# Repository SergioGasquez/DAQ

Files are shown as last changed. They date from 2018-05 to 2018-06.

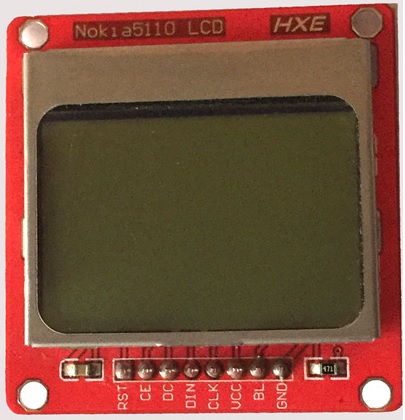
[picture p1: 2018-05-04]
LaTeX/Images/Nokia5110_Pinout.jpg

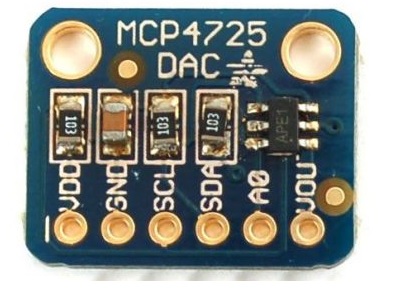
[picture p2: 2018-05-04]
LaTeX/Images/MCP4725_Pinout.jpg

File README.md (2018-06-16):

# Data Acquisition System

Here you can find everything about my final degree proyect, all the code, desings and PCB files can be found on the repository. Here is a summary of the proyect:

## General Diagram
The general diagram of the DAQ could be simplified as:

Diagram

Collected data will be avaliable in a [web developed for this purpose](https://tfg-sergio-gasquez.onlosant.com/) (An amazing IoT platform!)

## Prototypes
Two prototypes have been developed:

Propotype V1

Propotype V0

## Analog Conditioning
There are two analog conditioning parts:
- Amplifier

DAC DACanalog

-Reductor
ADC ADCanalog

Also, the MAX743 is used to power all the OP Amps in his typical configuration.

## Final product

This is the end result:

Result Propotype V1

The thesis can be also found in the repo, but sadly had to write it in spanish. If you have any doubt feel free to ask without hessitation!

## License
Copyright (c) 2017 Sergio Gasquez Licensed under the MIT license.

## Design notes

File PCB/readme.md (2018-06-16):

# PCB

## Schematic 

Schematic

## Layout 

Layout

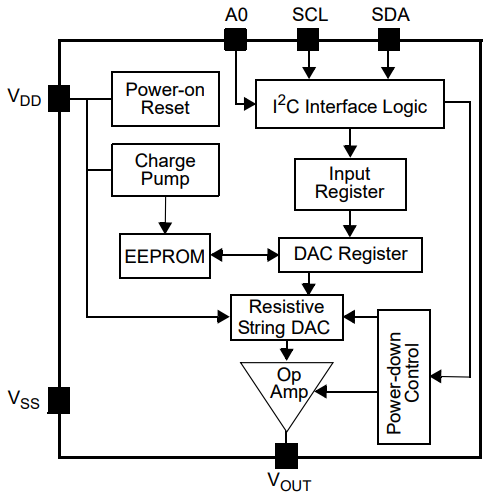
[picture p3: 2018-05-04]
LaTeX/Images/MCP4725_Schematic.PNG

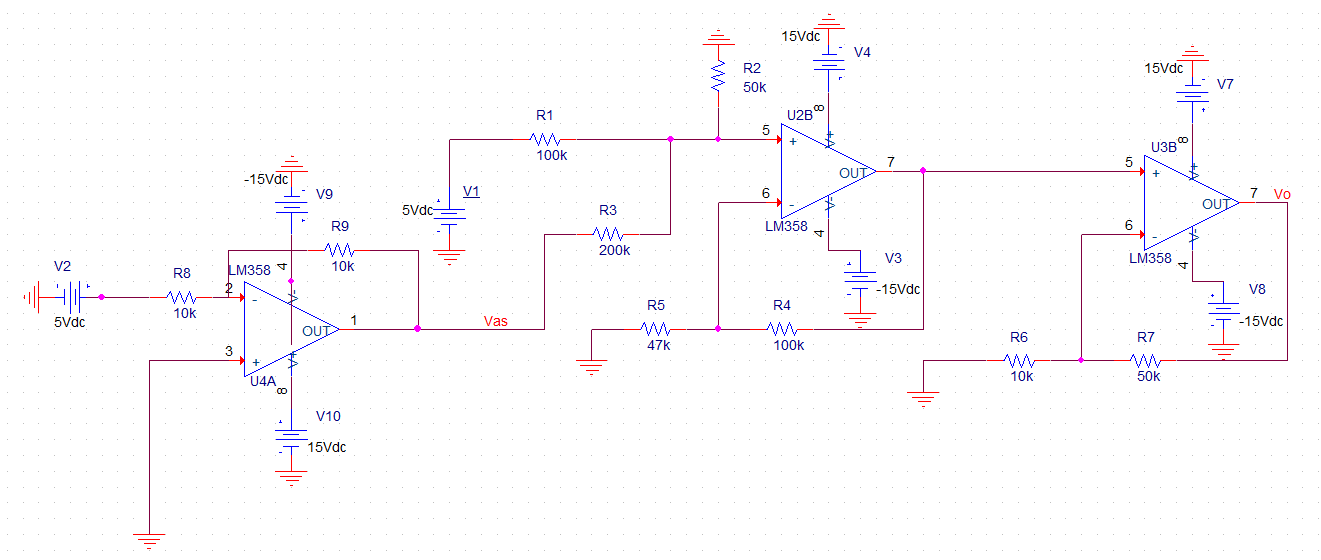
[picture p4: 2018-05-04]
LaTeX/Images/Amplificator_Schematic.PNG

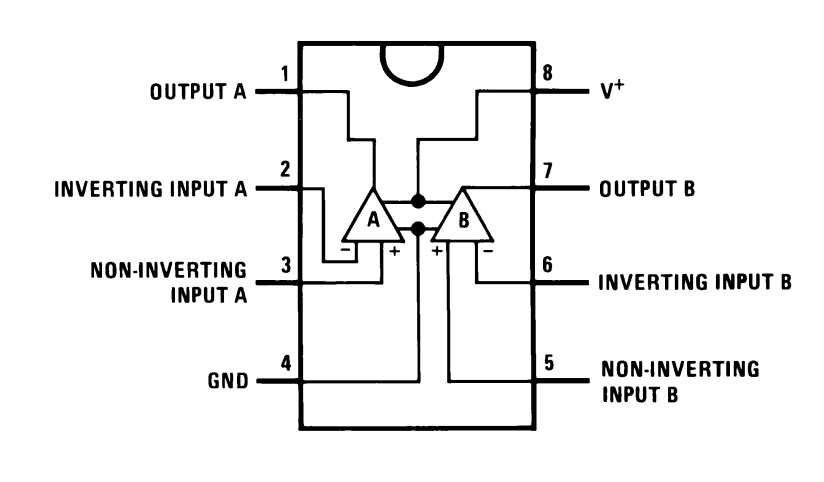
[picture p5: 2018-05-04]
LaTeX/Images/LM358_Pinout.PNG

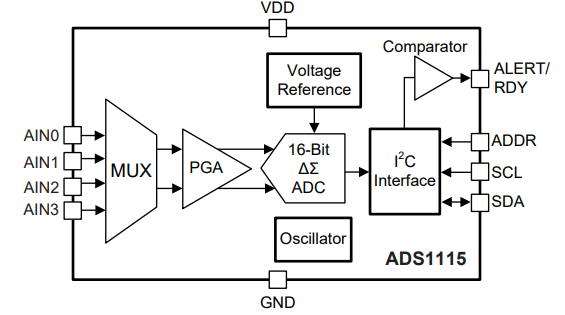
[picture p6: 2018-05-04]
LaTeX/Images/ADS1115_Schematic.PNG

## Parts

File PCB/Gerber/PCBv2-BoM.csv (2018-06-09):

Id | Designator | Package | Quantity | Designation | Supplier and ref
1 | U2 | SDShield | 1 | RTC
2 | J1 | arduino_mega_header | 1 | Arduino_Mega_Header
3 | U5 | ADC | 1 | ADC
4 | J2 | Pin_Header_Straight_1x10_Pitch2.54mm | 1 | Conn_01x10
5 | J3,J4,J7,J8,J6 | arduino_pin_socket_8 | 5 | Conn_01x08
6 | J5 | Pin_Header_Straight_2x18_Pitch2.54mm | 1 | Conn_02x18_Odd_Even
7 | U1 | Nokia5110 | 1 | NOKIA5110
8 | D3,D4,D5 | D_DO-15_P2.54mm_Vertical_AnodeUp | 3 | LM4040
9 | J9,J10,J11,J12,J13 | ScrewTerminal | 5 | Screw_Terminal_01x03
10 | R5,R14 | R-C-L-D | 2 | 200k
11 | R6 | R-C-L-D | 1 | 51k
12 | R7,R15 | R-C-L-D | 2 | 47k
13 | R8,R12,R16,R4 | R-C-L-D | 4 | 100k
14 | R9,R20,R3 | R-C-L-D | 3 | 22k
15 | R10,R11,R18,R23 | R-C-L-D | 4 | 10k
16 | R13,R19 | R-C-L-D | 2 | 50k
17 | R17 | R-C-L-D | 1 | 270k
18 | R21 | R-C-L-D | 1 | 1k
19 | R22 | R-C-L-D | 1 | 330
20 | U4 | DIP-16_W7.62mm | 1 | ADG408
21 | IC1 | DIP-16_W7.62mm | 1 | MAX743CWE+
22 | C1,C5 | Cap | 2 | 0.01uF
23 | C2 | Cap | 1 | 0.1uF
24 | C3 | Cap | 1 | 10uF
25 | C4 | Cap | 1 | 1uFC
26 | C6,C7,C11,C12,C13,C14,C15,C16,C17,C18,C19 | Cap | 11 | 100nF
27 | C8,C9,C10 | Cap | 3 | 100uF
28 | D1,D2 | R-C-L-D | 2 | D_Schottky
29 | L1,L2 | R-C-L-D | 2 | 100uH
30 | R1 | R-C-L-D | 1 | 68k
31 | R2 | R-C-L-D | 1 | 18k
32 | U6,U7,U8,U9,U10 | DIP-8_W7.62mm | 5 | LM358
33 | U11 | DAC | 1 | DAC
34 | U12 | DIP-8_W7.62mm | 1 | DG419
35 | U3 | SDShield | 1 | SDshield
36 | J14 | Pin_Header_Straight_1x05_Pitch2.54mm | 1 | Conn_01x05

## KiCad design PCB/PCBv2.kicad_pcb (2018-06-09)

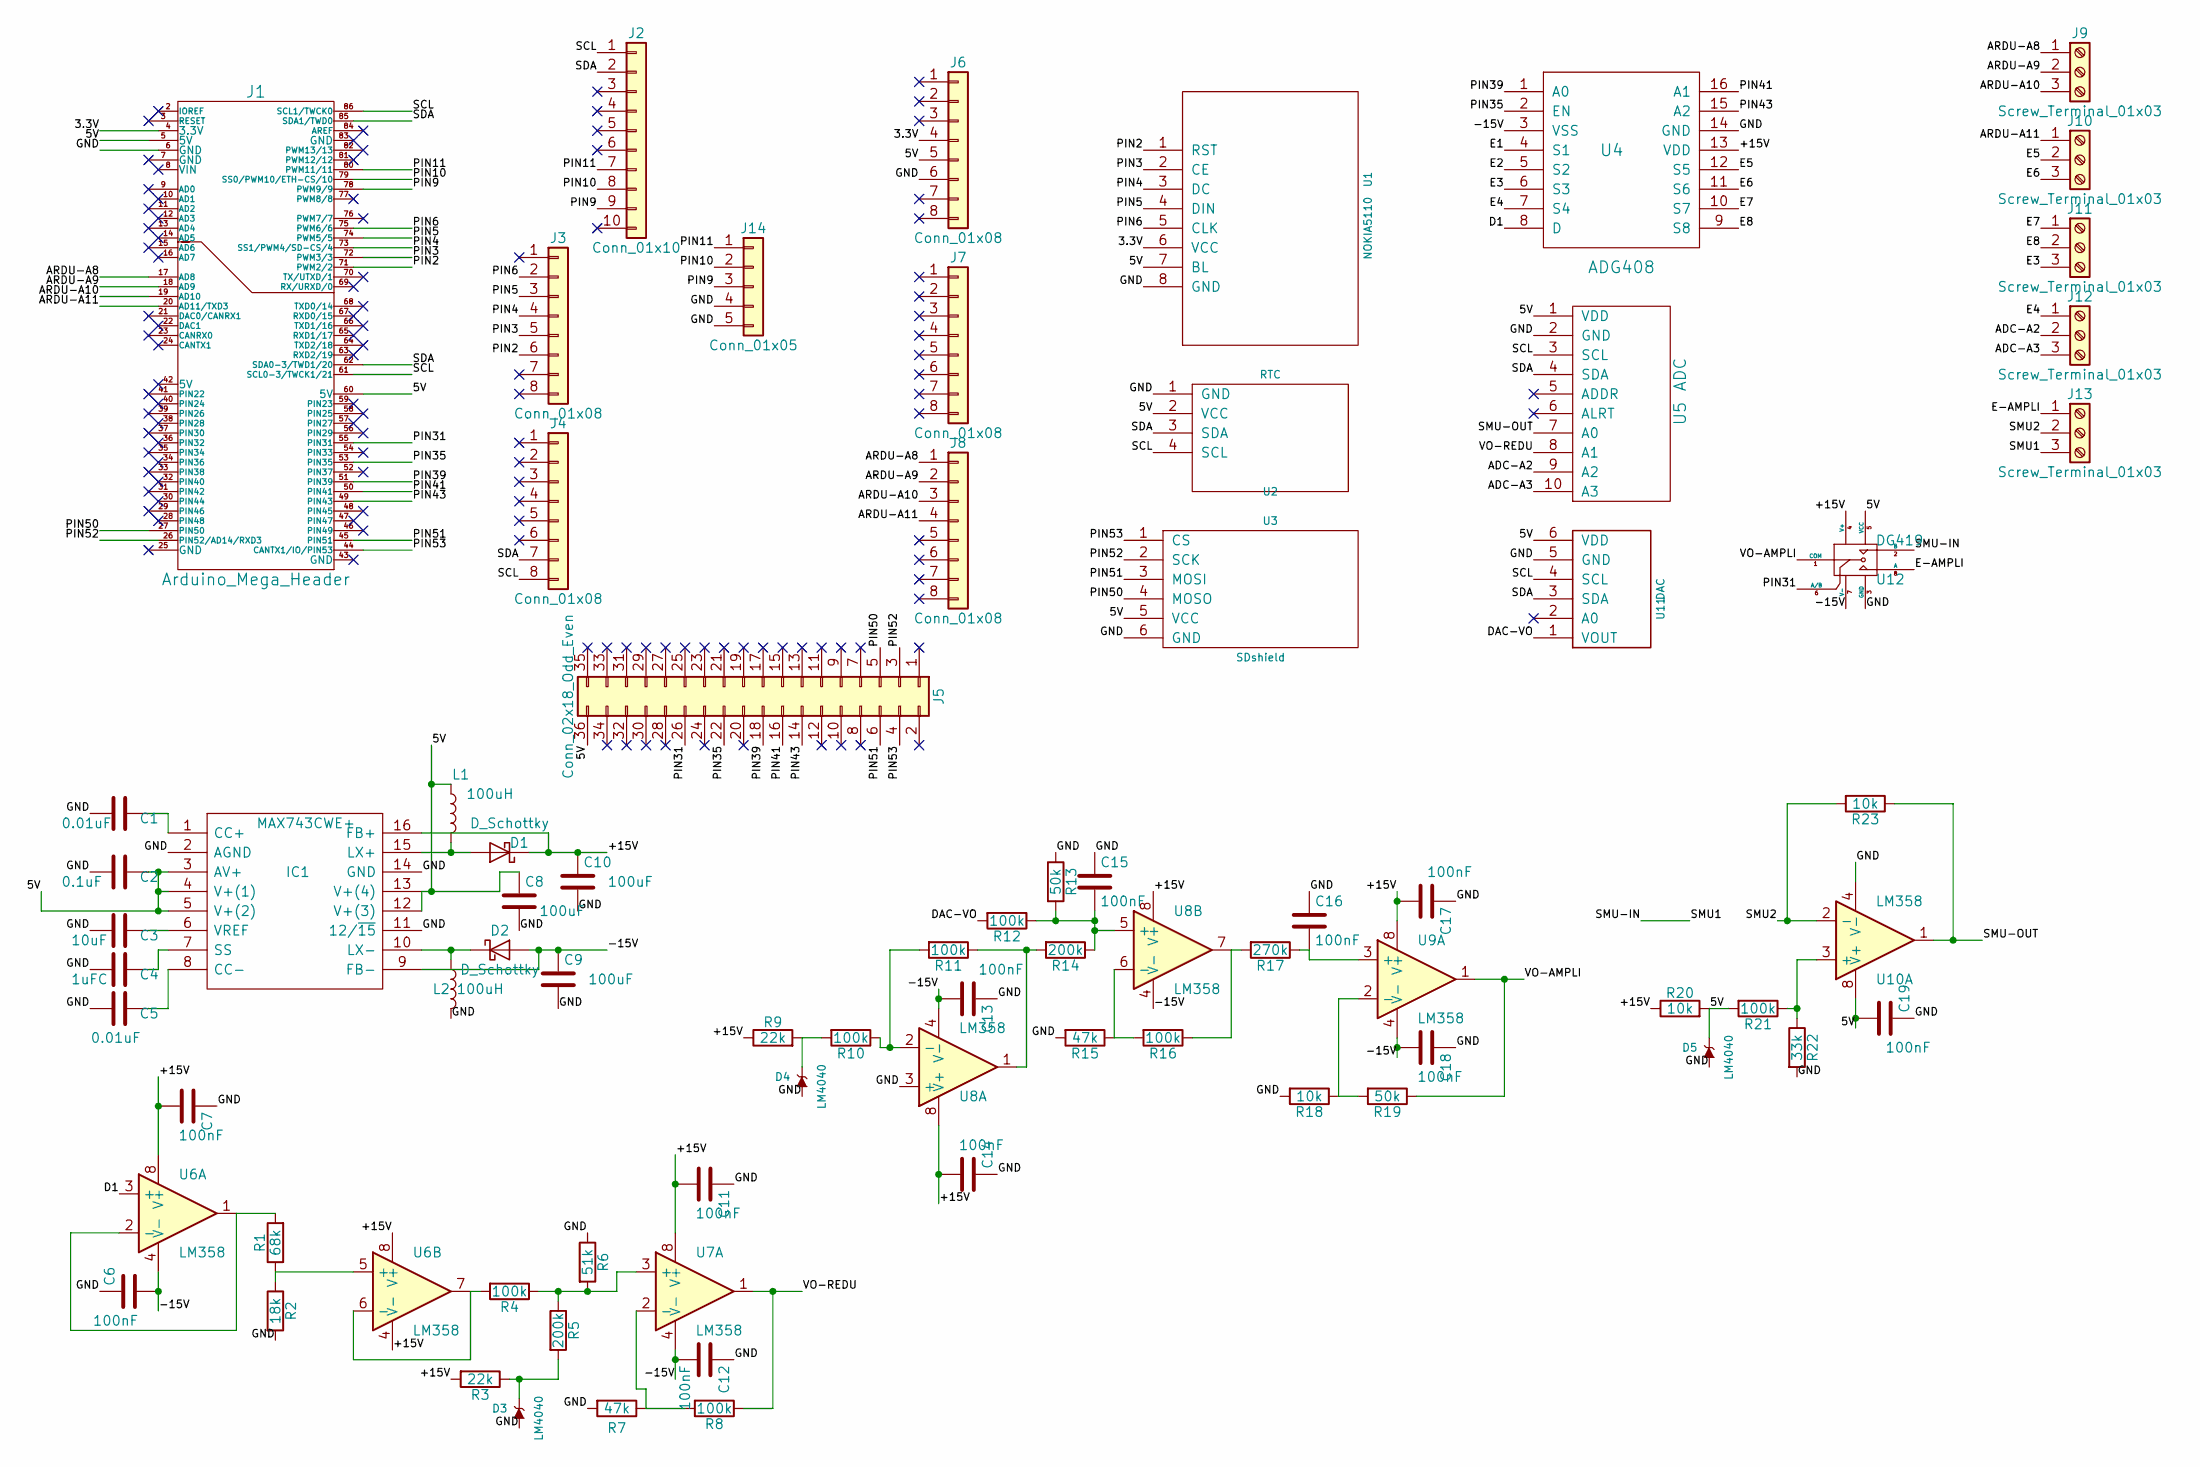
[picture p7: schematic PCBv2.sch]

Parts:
C1, C5: 0.01uF; Cap
C2: 0.1uF; Cap
C3: 10uF; Cap
C4: 1uFC; Cap
C6, C7, C11, C12, C13, C14, C15, C16, C17, C18, C19: 100nF; Cap
C8, C9, C10: 100uF; Cap
D1, D2: D_Schottky; R-C-L-D
D3, D4, D5: LM4040; D_DO-15_P2.54mm_Vertical_AnodeUp
IC1: MAX743CWE+; DIP-16_W7.62mm; Manufacturer_Part_Number MAX743CWE+
J1: Arduino_Mega_Header; arduino_mega_header
J2: Conn_01x10; Pin_Header_Straight_1x10_Pitch2.54mm
J3, J4, J6, J7, J8: Conn_01x08; arduino_pin_socket_8
J5: Conn_02x18_Odd_Even; Pin_Header_Straight_2x18_Pitch2.54mm
J9, J10, J11, J12, J13: Screw_Terminal_01x03; ScrewTerminal
J14: Conn_01x05; Pin_Header_Straight_1x05_Pitch2.54mm
L1, L2: 100uH; R-C-L-D
R1: 68k; R-C-L-D
R2: 18k; R-C-L-D
R3, R9: 22k; R-C-L-D
R4, R8, R10, R11, R12, R16, R21: 100k; R-C-L-D
R5, R14: 200k; R-C-L-D
R6: 51k; R-C-L-D
R7, R15: 47k; R-C-L-D
R13, R19: 50k; R-C-L-D
R17: 270k; R-C-L-D
R18, R20, R23: 10k; R-C-L-D
R22: 33k; R-C-L-D
U1: NOKIA5110; Nokia5110
U2: RTC; SDShield
U3: SDshield; SDShield
U4: ADG408; DIP-16_W7.62mm
U5: ADC
U6, U7, U8, U9, U10: LM358; DIP-8_W7.62mm
U11: DAC
U12: DG419; DIP-8_W7.62mm

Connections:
/3.3V: J1.4 (3.3V), J6.4, U1.6 (VCC)
/5V: C2.1, C8.1, C19.2, D5.1 (K), IC1.3 (AV+), IC1.4 (V+(1)), IC1.5 (V+(2)), IC1.12 (V+(3)), IC1.13 (V+(4)), J1.5 (5V), J1.60 (5V), J5.36, J6.5, L1.1, R20.2, R21.2, U1.7 (BL), U2.2 (VCC), U3.5 (VCC), U5.1 (VDD), U10.8 (V+), U11.6 (VDD), U12.5 (VCC)
/ADC-A2: J12.2, U5.9 (A2)
/ADC-A3: J12.3, U5.10 (A3)
/ARDU-A8: J1.17 (AD8), J8.1, J9.1
/ARDU-A9: J1.18 (AD9), J8.2, J9.2
/ARDU-A10: J1.19 (AD10), J8.3, J9.3
/ARDU-A11: J1.20 (AD11/TXD3), J8.4, J10.1
/D1: U4.8 (D), U6.3 (+)
/DAC-VO: R12.2, U11.1 (VOUT)
/E1: U4.4 (S1)
/E2: U4.5 (S2)
/E3: J11.3, U4.6 (S3)
/E4: J12.1, U4.7 (S4)
/E5: J10.2, U4.12 (S5)
/E6: J10.3, U4.11 (S6)
/E7: J11.1, U4.10 (S7)
/E8: J11.2, U4.9 (S8)
/E-AMPLI: J13.1, U12.8 (A)
/GND: C1.2, C2.2, C3.2, C4.2, C5.2, C6.1, C7.1, C8.2, C9.2, C10.2, C11.1, C12.1, C13.1, C14.1, C15.1, C16.1, C17.1, C18.1, C19.1, D3.2 (A), D4.2 (A), D5.2 (A), IC1.2 (AGND), IC1.11 (12/~15), IC1.14 (GND), J1.6 (GND), J6.6, J14.4, J14.5, L2.2, R2.2, R6.1, R7.2, R13.1, R15.2, R18.2, R22.2, U1.8 (GND), U2.1 (GND), U3.6 (GND), U4.14 (GND), U5.2 (GND), U8.3 (+), U10.4 (V-), U11.5 (GND), U12.3 (GND)
/PIN2: J1.71 (PWM2/2), J3.6, U1.1 (RST)
/PIN3: J1.72 (PWM3/3), J3.5, U1.2 (CE)
/PIN4: J1.73 (SS1/PWM4/SD-CS/4), J3.4, U1.3 (DC)
/PIN5: J1.74 (PWM5/5), J3.3, U1.4 (DIN)
/PIN6: J1.75 (PWM6/6), J3.2, U1.5 (CLK)
/PIN9: J1.78 (PWM9/9), J2.9, J14.3
/PIN10: J1.79 (SS0/PWM10/ETH-CS/10), J2.8, J14.2
/PIN11: J1.80 (PWM11/11), J2.7, J14.1
/PIN31: J1.55 (PIN31), J5.26, U12.6 (A/B)
/PIN35: J1.53 (PIN35), J5.22, U4.2 (EN)
/PIN39: J1.51 (PIN39), J5.18, U4.1 (A0)
/PIN41: J1.50 (PIN41), J5.16, U4.16 (A1)
/PIN43: J1.49 (PIN43), J5.14, U4.15 (A2)
/PIN50: J1.27 (PIN50), J5.5, U3.4 (MOSO)
/PIN51: J1.45 (PIN51), J5.6, U3.3 (MOSI)
/PIN52: J1.26 (PIN52/AD14/RXD3), J5.3, U3.2 (SCK)
/PIN53: J1.44 (CANTX1/IO/PIN53), J5.4, U3.1 (CS)
/SCL: J1.61 (SCL0-3/TWCK1/21), J1.86 (SCL1/TWCK0), J2.1, J4.8, U2.4 (SCL), U5.3 (SCL), U11.4 (SCL)
/SDA: J1.62 (SDA0-3/TWD1/20), J1.85 (SDA1/TWD0), J2.2, J4.7, U2.3 (SDA), U5.4 (SDA), U11.3 (SDA)
/SMU2: J13.2, R23.2, U10.2 (-)
/SMU-IN: J13.3, U12.2 (B)
/SMU-OUT: R23.1, U5.7 (A0), U10.1
/VO-AMPLI: R19.1, U9.1, U12.1 (COM)
/VO-REDU: R8.1, U5.8 (A1), U7.1
unnamed: C1.1, IC1.1 (CC+)
unnamed: C3.1, IC1.6 (VREF)
unnamed: C4.1, IC1.7 (SS)
unnamed: C5.1, IC1.8 (CC-)
unnamed: C15.2, R12.1, R13.2, R14.1, U8.5 (+)
unnamed: C16.2, R17.1, U9.3 (+)
unnamed: D1.2 (A), IC1.15 (LX+), L1.2
unnamed: D2.1 (K), IC1.10 (LX-), L2.1
unnamed: D3.1 (K), R3.1, R5.2
unnamed: D4.1 (K), R9.2, R10.2
unnamed: R1.1, R2.1, U6.5 (+)
unnamed: R1.2, U6.1, U6.2 (-)
unnamed: R4.1, R5.1, R6.2, U7.3 (+)
unnamed: R4.2, U6.6 (-), U6.7
unnamed: R7.1, R8.2, U7.2 (-)
unnamed: R10.1, R11.2, U8.2 (-)
unnamed: R11.1, R14.2, U8.1
unnamed: R15.1, R16.2, U8.6 (-)
unnamed: R16.1, R17.2, U8.7
unnamed: R18.1, R19.2, U9.2 (-)
unnamed: R21.1, R22.1, U10.3 (+)

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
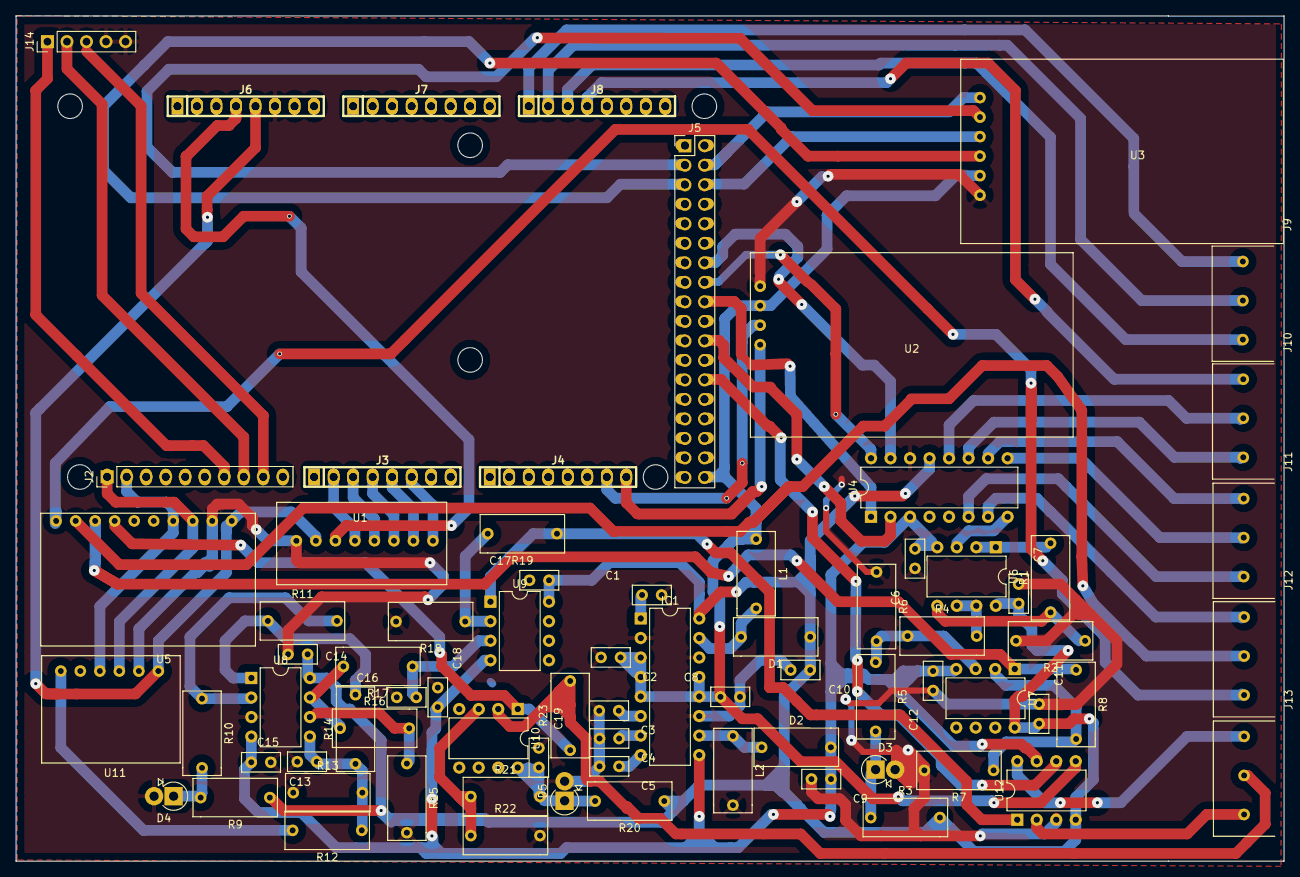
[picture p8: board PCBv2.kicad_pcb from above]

Board: 2 copper layers, 165.1 x 110.0 mm, 76 parts (1 on the bottom side), 65 nets.

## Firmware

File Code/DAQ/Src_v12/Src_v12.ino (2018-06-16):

/*
           Data Acquisition System
            Sergio Gasquez Arcos


       https://github.com/SergioGasquez/DAQ


*/

//-------------- DEFINES --------------//
#define LCD
#define RTC
#define microSD
#define ADC
#define DAC
#define MULTIPLEXER
#define MULTIPLEXER2
#define MEM_EEPROM
//#define COMGPRS
#define DEBUGGING true

//-------------- TIMERS --------------//
#define WTDG_CYCLES  10
#define COMM_TIME 60     // Time between comms (in seconds)
#define SD_TIME 1200    // Time between saves in the SD (in seconds)

#define maxCyclesComm (COMM_TIME/8)
#define maxCyclesSD (SD_TIME/8)



#include <Wire.h>
#include <avr/wdt.h>
#include <avr/sleep.h>


//-------------- SD --------------//
#ifdef microSD
#include <SPI.h>
#include <SD.h>
int pinCS = 53;
#endif //microSD


//-------------- GPRS --------------//
#ifdef COMGPRS
#include <SoftwareSerial.h>
SoftwareSerial SIM900(10, 11); // (RX, TX)
#endif //GPRS


//-------------- WTDG --------------//
volatile int ISRCounterWTDG = 0;


//-------------- ADC --------------//
#ifdef ADC
#include <Adafruit_ADS1015.h>
Adafruit_ADS1115 ads(0x48);     // ADC 0x48 is the default address
#endif //ADC

//-------------- DAC --------------//
#ifdef DAC
#include <Adafruit_MCP4725.h>
Adafruit_MCP4725 dac;
#endif //DAC

//-------------- RTC --------------//
#ifdef RTC
#include "RTClib.h"             // A5 ->SCL   A4 ->SDA
RTC_DS3231 rtc;
#endif //RTC

//-------------- LCD --------------//
#ifdef LCD
#include<LCD5110_Graph.h>
LCD5110 myGLCD(6, 5, 4, 2, 3);  // myGLCD(CLK,DIN,DC,RST,CE)
#endif //LCD

//-------------- MULTIPLEXER --------------//
#ifdef MULTIPLEXER
int enablePin = 35;
int multiplexerA0 = 39;
int multiplexerA1 = 41;
int multiplexerA2 = 43;
#endif //MULTIPLEXER

#ifdef MULTIPLEXER2
int multiplexer2Pin = 31;
#endif //MULTIPLEXER2


// File for SD
#ifdef microSD
File myFile;                      // Declare global file
String fileNameStr;               // File of the .txt
char fileName[12];

unsigned int sdCycles = 0;
volatile bool flagSD = true;
#endif //microSD

// Global Variables for date and time
#ifdef RTC
byte dayRTC;
byte monthRTC;
int yearRTC;
byte hoursRTC;
byte minutesRTC;
byte secondsRTC;
#endif //RTC

// Fonts and autonomous mode boolean
#ifdef LCD
extern uint8_t SmallFont[];
extern unsigned char TinyFont[];
bool autonomousMode = true;
#endif //LCD




#ifdef COMGPRS
unsigned int commCycles = 0;
volatile bool commFlag = false;
#endif // COMGPRS

char confStr1[9] = "9";
char confStr2[10] = "9";

// Cofiguration Variables
boolean smu = true;
boolean typeSMU = true;
boolean typeSignal = true;
boolean ADC_2 = true;
boolean ADC_3 = true;
boolean ARDU_A8 = true;
boolean ARDU_A9 = true;
boolean ARDU_A10 = true;
boolean ARDU_A11 = true;
boolean multi_E5 = true;
boolean multi_E6 = true;
boolean multi_E7 = true;
boolean multi_E8 = true;
boolean multi_E3 = true;
boolean multi_E4 = true;
byte operatingMode = 0;


// Channels values
int valSMU = 0;
int valADC_2 = 0;
int valADC_3 = 0;
int valArdu_A8 = 0;
int valArdu_A9 = 0;
int valArdu_A10 = 0;
int valArdu_A11 = 0;
int valMulti_E5 = 0;
int valMulti_E6 = 0;
int valMulti_E7 = 0;
int valMulti_E8 = 0;
int valMulti_E3 = 0;
int valMulti_E4 = 0;
int dacVal = 0;



//-------------- FUNCTIONS --------------//
void(* ResetSW) (void) = 0;


/*        Watchdog Interrup Function
   ----------------------------------------
   Each time watcdog interrupt is triggered
   (and it will be triggered each 8 secs)
   this function will run.

   We increment in 1 all the counters and if
   any counter has reach his max, it activates
   the flag.

*/

ISR (WDT_vect)
{
  ISRCounterWTDG++;
#if DEBUGGING
  //Serial.print("WTDG: ");Serial.println(ISRCounterWTDG);
#endif //DEBUGGING
  if (ISRCounterWTDG >= WTDG_CYCLES)
  {
    delay(50);
    ISRCounterWTDG = 0;
#if DEBUGGING
    Serial.println("Reset due to WTDG");
#endif //DEBUGGING
    delay(1000);
    ResetSW();
  }
#ifdef COMGPRS
  commCycles++;
  if (commCycles >= maxCyclesComm)
  {
    commFlag = true;
    commCycles = 0;
#if DEBUGGING
    //Serial.println("commFlag");
#endif //DEBUGGING  
  }
#if DEBUGGING
  //Serial.print("commCycles: "); Serial.println(commCycles);
#endif //DEBUGGING  
#endif //COMGPRS

#ifdef microSD
  sdCycles++;
#if DEBUGGING
  //Serial.print("sdCycles: "); Serial.println(sdCycles);
#endif //DEBUGGING
  if (sdCycles >= maxCyclesSD)
  {
    flagSD = true;
    sdCycles = 0;
#if DEBUGGING
    //Serial.print("flagSD: "); Serial.println(flagSD);
#endif //DEBUGGING  
  }
#endif //microSD
}// Final ISR

/*                Flash
   ----------------------------------------
   It makes the builtin flash in order
   to debug without a Serial Monitor
*/

void flash()
{
  digitalWrite(13, HIGH);
  delay(500);
  digitalWrite(13, LOW);
  delay(500);
}

void setup()
{
  Serial.begin(9600);
  delay(500);
#ifdef RTC
  initRTC();
#endif //RTC


#ifdef DAC
  dac.begin(0x62);        // Default address for MCP4725A1
  delay(500);
  //dac.setVoltage(1640, false);

#endif //DAC

#ifdef ADC
  ads.begin();
  delay(500);
#endif //ADC

#ifdef LCD
  myGLCD.InitLCD();
  myGLCD.setFont(SmallFont);
  randomSeed(analogRead(7));
  delay(100);
  updateTaskLCD(0);
#endif //LCD

#ifdef COMGPRS
  initSIM900();
  delay(1000);
#endif //COMGPRS
  setWatchdog();

#ifdef MEM_EEPROM
  checkIfConnected();
  configureSystem();
#endif // MEM_EEPROM

#ifdef microSD
  initSD();
#endif //microSD


#ifdef MULTIPLEXER
  initMultiplexer();
#endif // MULTIPLEXER
  flash();
#ifdef COMGPRS
  if (strlen(confStr1) > 2)
  {
    sendConfig();
  }
#endif //COMGPRS
}

void loop()
{
  if (operatingMode == 0)
  {
    ResetWTDG();
    cpuSleep();
#ifdef COMGPRS
    if (commFlag)
    {
      updateTaskLCD(1);
      ResetWTDG();
      commFlag = false;
#if DEBUGGING
      Serial.println("Data will be sent...");
#endif DEBUGGING
#ifdef LCD
      updateTaskLCD(3);
#endif // LCD
      measureChannels();
      delay(1000);
#ifdef LCD
      updateTaskLCD(1);
#endif // LCD
      sendData();
#ifdef LCD
      updateConfigLCD();
#endif // LCD
    }
#endif // COMGPRS

#ifdef microSD
    if (flagSD)
    {
      ResetWTDG();
      flagSD = false;
#if DEBUGGING
      Serial.println("Data will be saved in the SD Card");
#endif //DEBUGGING
#ifdef LCD
      updateTaskLCD(3);
#endif // LCD
      measureChannels();
      delay(2000);
      updateTaskLCD(2);
      getTime();
      saveToSD();
      delay(2000);
#ifdef LCD
      updateConfigLCD();
#endif// LCD;
    }
#endif //microSD
  }
  if (operatingMode == 1)     // Voltage Sweep
  {
    Serial.println("Voltage Sweep");
    int counter;
    for (counter = 0; counter < 20; counter++)
    {
      ResetWTDG();
#if DEBUGGING
      Serial.print("dacVal: "); Serial.println(dacVal);
#endif //DEBUGGIN
      dacVal = counter * 100;
      dac.setVoltage(dacVal, false);
      getTime();
#ifdef LCD
      updateTaskLCD(3);
#endif// LCD;
      measureChannels();
#ifdef LCD
      updateTaskLCD(1);
#endif// LCD;
#ifdef COMGPRS
      sendData();
#endif // COMGPRS
#ifdef LCD
      updateTaskLCD(2);
#endif// LCD;
      saveToSD();
    }
  }

  if (operatingMode == 2)       // Generate Wave form
  {
    if (typeSignal)
    {
      generateWaveform(0);
    }
    if (!typeSignal)
    {
      generateWaveform(1);
    }
  }

}

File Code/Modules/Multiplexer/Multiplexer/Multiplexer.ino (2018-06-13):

int enablePin = 35;
int multiplexerA0 = 39;
int multiplexerA1 = 41;
int multiplexerA2 = 43;



void initMultiplexer()
{
  pinMode(enablePin, OUTPUT);
  pinMode(multiplexerA0, OUTPUT);
  pinMode(multiplexerA1, OUTPUT);
  pinMode(multiplexerA2, OUTPUT);

  digitalWrite(enablePin, HIGH);
  Serial.println("Multiplexer Initialized");
}


/*              setChannel
   ----------------------------------------
   Funtion that selects which channel of
   the multiplexer will be conected to
   the output.
*/
void setChannel(byte channel)
{                        
  if (channel == 1)
  {
    digitalWrite(multiplexerA0, LOW);
    digitalWrite(multiplexerA1, LOW);
    digitalWrite(multiplexerA2, LOW);
  }
  else if (channel == 2)
  {
    digitalWrite(multiplexerA0, HIGH);
    digitalWrite(multiplexerA1, LOW);
    digitalWrite(multiplexerA2, LOW);
  }
  else if (channel == 3)
  {
    digitalWrite(multiplexerA0, LOW);
    digitalWrite(multiplexerA1, HIGH);
    digitalWrite(multiplexerA2, LOW);
  }
  else if (channel == 4)
  {
    digitalWrite(multiplexerA0, HIGH);
    digitalWrite(multiplexerA1, HIGH);
    digitalWrite(multiplexerA2, LOW);
  }
  else if (channel == 5)
  {
    digitalWrite(multiplexerA0, LOW);
    digitalWrite(multiplexerA1, LOW);
    digitalWrite(multiplexerA2, HIGH);
  }
  else if (channel == 6)
  {
    digitalWrite(multiplexerA0, HIGH);
    digitalWrite(multiplexerA1, LOW);
    digitalWrite(multiplexerA2, HIGH);
  }
  else if (channel == 7)
  {
    digitalWrite(multiplexerA0, LOW);
    digitalWrite(multiplexerA1, HIGH);
    digitalWrite(multiplexerA2, HIGH);
  }
  else if (channel == 8)
  {
    digitalWrite(multiplexerA0, HIGH);
    digitalWrite(multiplexerA1, HIGH);
    digitalWrite(multiplexerA2, HIGH);
  }
  else
  {
    Serial.println("Error. Wrong channel");
  }
}

void setup() {
  initMultiplexer();
  Serial.begin(9600);
}

void loop() {
  Serial.println("5");
  setChannel(5);
  delay(5000);
  Serial.println("6");
  setChannel(6);
  delay(5000);
  Serial.println("7");
  setChannel(7);
  delay(5000);
  Serial.println("8");
  setChannel(8);
  delay(5000);
  Serial.println("3");
  setChannel(3);
  delay(5000);
  Serial.println("4");
  setChannel(3);
  delay(5000);

  
}

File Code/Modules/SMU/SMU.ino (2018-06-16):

/**************************************************************************/
/*!
    @file     trianglewave.pde
    @author   Adafruit Industries
    @license  BSD (see license.txt)

    This example will generate a triangle wave with the MCP4725 DAC.

    This is an example sketch for the Adafruit MCP4725 breakout board
    ----> http://www.adafruit.com/products/935

    Adafruit invests time and resources providing this open source code,
    please support Adafruit and open-source hardware by purchasing
    products from Adafruit!
*/
/**************************************************************************/
#include <Wire.h>
#include <Adafruit_MCP4725.h>
#include <Adafruit_ADS1015.h>

Adafruit_MCP4725 dac;
/*DAC*/
Adafruit_ADS1115 ads(0x48);
float Voltage = 0.0;
int multiplexer2Pin = 31;


int  dacVal;

void setup(void) {
  Serial.begin(9600);

  dac.begin(0x62); // Default address for MCP4725A1

  ads.begin();    // Initalice the adc

  //pinMode(multiplexer2Pin, OUTPUT);
  //digitalWrite(multiplexer2Pin, LOW);

}


float readADC(int channel)
{
  float aux = 0;
  int i = 0;
  for (i = 0; i <= 99; i++)
  {
    aux += ads.readADC_SingleEnded(channel);
  }
  aux = aux / 100;
  return aux;
}

void loop(void) {
  uint32_t counter;
  float valADC_A0;
  float voltage;
  counter = 0;
  //  for (counter = 0; counter < 9; counter++)  // Ramp       [-15,0] V
  //  {
  //    dacVal = counter * 205;
  //    Serial.print(" \tDAC: "); Serial.print(dacVal);
  //    dac.setVoltage(dacVal, false);
  //    delay(500);
  //    valADC_A0 = readADC(0);
  //    Serial.print(" \t ");Serial.println(valADC_A0);
  //  }
  valADC_A0 = readADC(2);
  //voltage = valADC_A0 * 0.1875;

  Serial.println(valADC_A0);
  //Serial.print("\t temp: "); Serial.println(voltage/10);

  delay(100);


  dacVal = 1650;
    for (counter = 0; counter < 25; counter++)  // Ramp       [-5,0] V
    {
      Serial.print(counter);
      dacVal += 2;
      Serial.print(" \tDAC: "); Serial.print(dacVal);
      dac.setVoltage(dacVal, false);             // We set the voltage at the counter valuex
      delay(500);
      valADC_A0 = readADC(0);
      voltage = valADC_A0 * 0.1875 / 1000;
      Serial.print("\t voltage: "); Serial.println(voltage);
  
    }
}

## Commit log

2018-03-11 Change of the structure and add PCB schematic
    [DAQ.kicad_pcb, DAQ.sch]
2018-03-12 PCB Improvement
    [DAQ.kicad_pcb, DAQ.sch]
2018-03-16 PCB Improvements
    [DAQ.kicad_pcb, DAQ.sch]
2018-03-16 Add ground plane,max743 and started analogic conditioner
    [DAQ.kicad_pcb, DAQ.sch]
2018-03-20 Analog Conditioner added int PCB layout
    [DAQ.kicad_pcb, DAQ.sch]
2018-04-03 Changed RTC module on PCB
    [DAQ.kicad_pcb, DAQ.sch]
2018-04-05 Add simulations of the analog part after the DAC
    [AMPLIFIER.DSN, DAQANALOGIC.DSN, LEVELSHIFTER.DSN]
2018-04-05 Improvements on the PCB
    [DAQ.kicad_pcb, DAQ.sch]
2018-04-06 Changes on simulations
    [DAQANALOGIC.DSN]
2018-04-10 Added analog part of DAC to PCB
    [DAQ.kicad_pcb, DAQ.sch]
2018-04-17 Analog parts of the PCB upgraded
    [DAQ.kicad_pcb, DAQ.sch, DAQANALOGIC.DSN]
2018-04-18 PCB Upgraded and screens of the DAC analog
    [DAC_Original_-15to15.CSV, DAC_Original_-15to15_NOISE.csv, DAC_Original_0to5.csv, DAQ.kicad_pcb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]
2018-04-24 Code modulation and PCB improvements. Multiplexer added
    [DAQ.kicad_pcb, DAQ.sch]
2018-05-04 Start of LaTeX proyect and few improvements
    [DAQ.kicad_pcb, DAQ.sch, Reductor.dsn]
2018-05-14 Added SMU,changes on Latex and new simulations
    [AmplifierHPF.dsn, DAQANALOGIC.DSN, SMU.DSN]
2018-05-19 New version of PCB
    [DAQ.kicad_pcb, DAQ.sch, PCBv2.kicad_pcb, PCBv2.sch]
2018-05-20 Added photos of the prototype and changed the PCB
    [PCBv2.kicad_pcb, PCBv2.sch]
2018-05-23 Changes on PCB and pins of LCD
    [PCBv2.kicad_pcb, PCBv2.sch]
2018-05-29 Added GPRS communications and lots of changes on the main code!
    [PCBv2-B.Cu.gbr, PCBv2-B.SilkS.gbr, PCBv2-F.Cu.gbr, PCBv2-F.SilkS.gbr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]
2018-06-04 Added pwr pin of the SIM900 and documentation made
    [PCBv2.kicad_pcb, PCBv2.sch]
2018-06-05 Changes on PCB track width and small track changes
    [PCBv2-B.Cu.gbr, PCBv2-B.SilkS.gbr, PCBv2-F.Cu.gbr, PCBv2-F.SilkS.gbr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]
2018-06-09 Added output via terminal and voltage sweep for I/V curves with the SMU
    [PCBv2-BoM.csv, PCBv2.kicad_pcb, PCBv2.sch]
2018-06-13 Added some missing images for the latex thesis and small changes in code
    [PCBv2.sch, SMU.DSN]
2018-06-16 Reorganized some directories, added the thesis pdf and latex files
    [DAC_Original_-15to15.CSV, DAC_Original_-15to15_NOISE.csv, DAC_Original_0to5.csv, DAQ.kicad_pcb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]
2018-06-16 Add a readme on PCB
